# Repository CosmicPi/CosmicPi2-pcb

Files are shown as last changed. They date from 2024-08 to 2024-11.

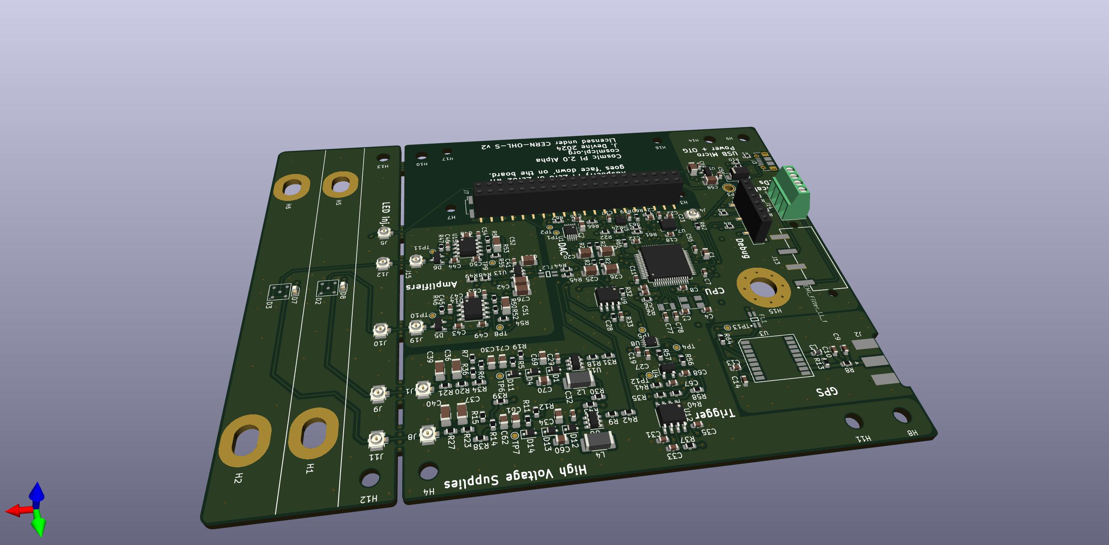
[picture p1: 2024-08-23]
3drenderthird.jpg

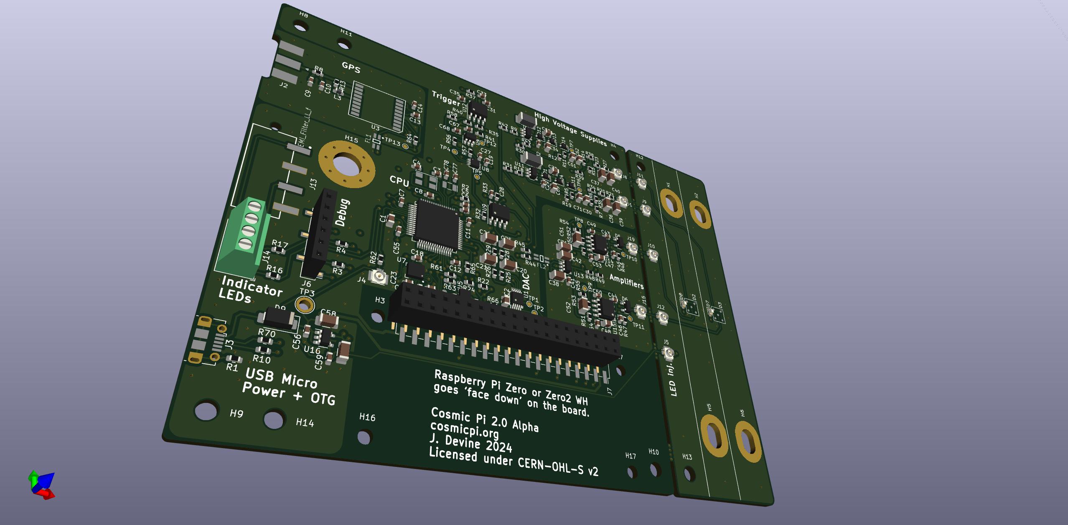
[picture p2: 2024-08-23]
3drendersecond.jpg

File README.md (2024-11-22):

# CosmicPiV2.0b
Version 2, beta production of the Cosmic Pi, learning the lessons from V2.0alpha and adding back the UART connection between GPS and STM32. All the components are now on a single PCB with a snap-off for the SiPM elements. SiPMs are now from Broadcom, as they purchased Ketek's SiPM production unit.

The design uses scintillators from Amcrys http://www.amcrys.com/ which are not yet available via a retail outlet, however any BC-408 equivalent scintillator that has diamond polished finish surfaces and dimensions of 200x100x10mm can be mated to the SiPMs with suitable mounting holes.

# What do the signals do?
To be added

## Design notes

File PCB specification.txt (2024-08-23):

Cosmic Pi PCB specification
Base material: FR-4
Number of layers: 4
PCB dimensions: 130mmx185mm
PCB thickness: 1.6mm
PCB colour: Green
Surface finish: HASL lead free
Minimum Solder Mask Dam: 0.4mm
Copper weight: 1 oz
Minimum Drill Hole Size: 0.3mm
Trace width/spaceing: 6/6 mil
Plated half holes/castellated holes: No
Impedance control: No

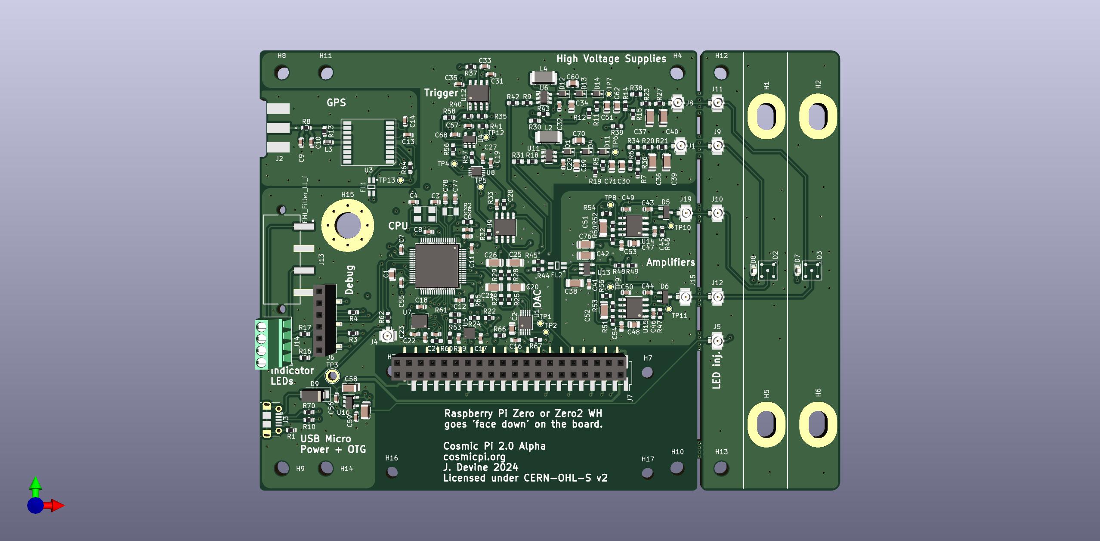
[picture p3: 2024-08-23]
3drenderfirst.jpg

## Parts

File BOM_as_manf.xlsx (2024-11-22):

Item # | *Designator | *Qty | Manufacturer | *Mfg Part # | Description / Value | *Package/Footprint | Category | Your Instructions / Notes
1 | J7 | 1 | Harwin | M20-7872042 | 40 pin socket (2x20) for Raspberry Pi Zero | PinSocket_2x20_P2.54mm_Vertical_SMD | SMD
2 | R1,R16,R4,R3,R17,R70,R10 | 7 | Yageo | RC0603FR-0720RL | 20 Ohm resistor, 1%, 0.1W | R_0603_1608Metric | SMD
3 | C71,C34,C69,C61 | 4 | Murata | GCJ21BR72A104KA01K | 1u, 100V DC, 10% | C_0805_2012Metric | SMD
4 | R62 | 1 | Yageo | RC0603JR-07300RL | 300 Ohm resistor, 1% | R_0603_1608Metric | SMD
5 | C40,C75,C25,C37,C26,C21,C20,C36,C42,C58,C38,C39 | 12 | KYOCERA AVX | 12061C105KAZ2A | 1u, 100V DC, 10% | C_1206_3216Metric | SMD
6 | C62,C30 | 2 | Kemet | C0805C473K1RACTU | 47n, 100V, 10% | C_0805_2012Metric | SMD
7 | D5,D6 | 2 | Vishay | BAS70-04-G3-08 |  | SOT-23 | SMD
8 | U14,U15 | 2 | Analog Devices | AD8538ARZ | AD8039 | SOIC-8_3.9x4.9mm_P1.27mm | SMD
9 | C23,C55,C35,C5,C14,C43,C15,C6,C18,C7,C27,C11,C67,C49,C53,C50,C44,C54,C12,C8,C17, C16 | 22 | Kemet | C0603C104K4RACTU | 100n, 16V, 10% | C_0603_1608Metric | SMD
10 | R22,R25,R28,R24,R26,R49,R35,R7,R29,R15 | 10 | ROHM | MCR03EZPFX2202 | 10k, 1% | R_0603_1608Metric | DNS | CRG0603F10K
11 | FL1,FL2 | 2 | Wurth | 744232090 | Wire wound EMI filter | IND_744232090 | SMD | DLW31SN900SQ2L
12 | C70,C60 | 2 | Samsung | CL21B104KBCNNNC | 0.1u, 50V, 10% | C_0805_2012Metric | SMD
13 | U5 | 1 | Bosch | BME280 | Bosch humidity sensor BME280 | Bosch_LGA-8_2.5x2.5mm_P0.65mm_ClockwisePinNumbering | SMD
14 | U6,U11 | 2 | Analog Devices | MAX5026EUT-T | MAX5026EUT_ | SOT-23-6 | SMD | MAX5026EUT+T
15 | R63,R34,R64,R36,R39,R31,R59,R66,R57,R44,R38,R42,R61,R45,R60,R67,R30,R56,R58,R43,R8,R68,R69 | 21 | Yageo | RC0603JR-070RL | 0 ohm jumper, 5%, 0.1W | R_0603_1608Metric_Pad0.98x0.95mm_HandSolder | SMD
16 | R46,R47 | 2 | Yageo | RC0603FR-075K1L | 5.1k Ohm resistor, 1%, 0.1W | R_0603_1608Metric | SMD
17 | U16,U13 | 2 | Texas Instruments | LP2985-33DBVR | LP2985-3.3 | SOT-23-5 | SMD
18 | J13 | 1 | Wurth | 691709710304 | 691709710304 wurth 4 pin screw terminal. | 691709710304 | TH
19 | C59,C31,C41,C22 | 4 | Samsung | CL10B103KB8NNNC | 10n, 10%, 50V | C_0603_1608Metric | SMD
20 | U12 | 1 | onsemi | LM555CM | LM555 timer IC | SOIC-8_3.9x4.9mm_P1.27mm | SMD | TLC555ID
21 | L4,L2 | 2 | Murata | #A915BY-470M=P3 | 47u, 750mA | D53LC, 2020 | SMD | A915BY-470M=P3
22 | C32,C29,C19,C28,C68 | 5 | Murata | GCM188R71E105KA64D | 1u, 10%, 25V | C_0603_1608Metric | SMD
23 | J5,J9,J1,J4,J11,J10,J15,J12,J19,J8 | 10 | Hirose | U.FL-R-SMT(01) | u.FL socket | U.FL_Hirose_U.FL-R-SMT-1_Vertical | SMD
24 | C46,C45 | 2 | Kemet | C0603C300J5GACTU | 30p, 5%, 50V | C_0603_1608Metric | SMD
25 | D11,D12,D1,D4,D14,D13 | 6 | onsemi | 1N4148WS | 1N4148 | D_SOD-323F | SMD
26 | Y2 | 1 | Euroquartz | EQ161-32.768-9 | 32.768KHz | Crystal_SMD_EuroQuartz_EQ161-2Pin_3.2x1.5mm | SMD | ABS07-32.768KHZ-9-T
27 | R50,R21,R27,R20,R51,R23 | 6 | TE conectivity | CRG0603F1K0 | 1k, 1% 0.1W | R_0603_1608Metric | SMD
28 | R48 | 1 | Panasonic | ERA3AEB203V | 20k, 0.1%, 0.1W | R_0603_1608Metric | SMD
29 | C13,C24, C2 | 3 | Murata | GRM188R61A106ME69D | 10u, 10%, 10V | C_0603_1608Metric | SMD
30 | C77,C78 | 2 | TDK | CGA3E2C0G2A040C080AA | 4.3p, 100V | C_0603_1608Metric | SMD
31 | L3 | 1 | EPCOS | B82496C3470J000 | 47nH | L_0603_1608Metric | SMD
32 | C4,C3 | 2 | Syfer | 0603Y1000220JCT | 22p, 5%, 100V | C_0603_1608Metric | SMD
33 | C1 | 1 | Samsung | CL21B475KOFNNNG | 4.7u, 10%, 16V | C_0805_2012Metric | SMD
34 | R32,R33 | 2 | TE conectivity | CRG0603F330R | 330R, 1% 0.1W | R_0603_1608Metric | SMD | RC0603JR-07300RL
35 | R52,R53 | 2 | Panasonic | ERA3AEB303V | 30k, 0.1%, 0.1W | R_0603_1608Metric | SMD
36 | C47,C48 | 2 | Yageo | CC0603KRX7R9BB104 | 100n, 50V, 10% | C_0805_2012Metric | SMD | C0805C104K5RACTU
37 | Y1 | 1 | RALTRON | QC5CA8.00000F12B23R | 8 MHz | Crystal_SMD_5032-4Pin_5.0x3.2mm | SMD | LFXTAL061627
38 | D9 | 1 | Vishay | B140-E3/61T | B140-E3 | D_SMA | SMD
39 | R41,R37,R40,R2 | 4 | Vishay | CRCW0603100KFKEA | 100k, 1%, 0.1W | R_0603_1608Metric | SMD
40 | J3 | 1 | Molex | 105017-0001 | USB_B_Micro | USB_Micro-B_Molex-105017-0001 | SMD | 1050170001
41 | U9 | 1 | Maxim | MAX991ESA+ | MAX991 | SOIC-8_3.9x4.9mm_P1.27mm | SMD
42 | U7 | 1 | ST | LSM9DS1TR | LSM9DS1 | LGA-24L_3x3.5mm_P0.43mm | SMD
43 | R6,R14 | 2 | Vishay | CRCW0603200KFKEA | 200k, 1%, 0.1W | R_0603_1608Metric | SMD
44 | D8,D7 | 2 | Kingbright | KPH-1608QBC-D | LED | LED_0603_1608Metric | SMD | 150060BS84000
45 | R54,R55 | 2 | Panasonic | ERJ3EKF1000V | 100, 1%, 0.1W | R_0603_1608Metric | SMD
46 | J6 | 1 | Multicomp | 2211SM-06G-B1-TB | Programming header | PinSocket_1x06_P2.54mm_Vertical_SMD_Pin1Left | SMD
47 | C56 | 1 | TDK | C1608X5R1A226M080AC | 22u, 10V, 20% | C_0603_1608Metric | SMD
48 | J2 | 1 | Molex | 73251-1150 | SMA | SMA_Molex_73251-1153_EdgeMount_Horizontal | Edge
49 | U3 | 1 | Quectel | L76-M33 | L76-M33 | LM76-M33 | SMD
50 | U8 | 1 | Texas Instruments | SN74AUC2G32DCUR | 74AUC2G32 | VSSOP-8_2.4x2.1mm_P0.5mm | SMD
51 | R12,R19 | 2 | Vishay | CRCW06036K81FKEA | 6.81k, 1% 0.1W | R_0603_1608Metric | SMD
52 | U1 | 1 | Microchip | MCP4728-E/UN | MCP4728 | MSOP-10_3x3mm_P0.5mm | SMD
53 | R5,R11 | 2 | TE conectivity | CPF0603B255KE1 | 255k, 1%, 0.063W | R_0603_1608Metric | SMD
54 | U4 | 1 | Diodes incorporated | 74AHC1G00W5-7 | 74AHC1G00 | SOT-23-5 | SMD
55 | C76 | 1 | Taiyo Yuden | JMK316BBJ107MLHT | 100u, 20%, 6.3V | C_1206_3216Metric | SMD
56 | R13 | 1 | Vishay | CRCW060310R0FKEA | 10, 1%, 0.1W | R_0603_1608Metric | SMD
57 | U2 | 1 | ST | STM32F401RET6 | STM32F401RETx | LQFP-64_10x10mm_P0.5mm | SMD
58 | R9,R18 | 2 | Panasonic | ERA3AEB1372V | 13.7k, 0.1%, 0.1W | R_0603_1608Metric | SMD | ERA-3AEB1372V
59 | D2,D3 | 2 | Broadcom | AFBR-S4N44P014M | SiPM diode for single photon detection | AFBR-S4N44P014M | SMD
60 | C33 | 1 | Yageo | CC0603KRX7R8BB224 | 220n, 25V 10% | C_0603_1608Metric | SMD

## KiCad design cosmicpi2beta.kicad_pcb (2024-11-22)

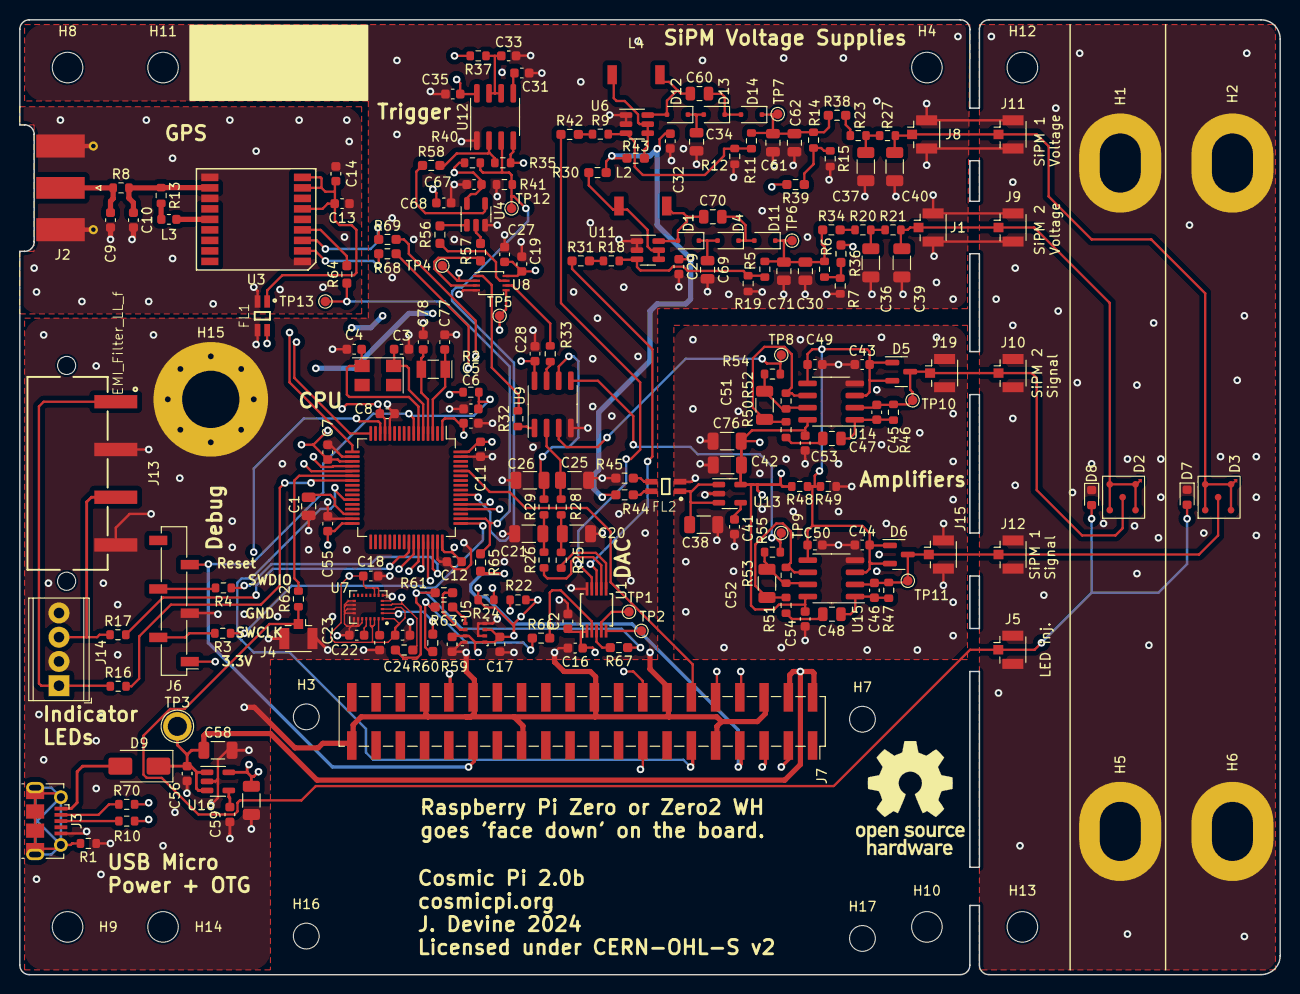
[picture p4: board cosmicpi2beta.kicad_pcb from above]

Board: 4 copper layers, 132.0 x 100.0 mm, 221 parts (0 on the bottom side), 122 nets.

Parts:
C1: 4.7u; C_0805_2012Metric
C2, C13, C24: 10u; C_0603_1608Metric
C3, C4: 22p; C_0603_1608Metric
C5, C6, C7, C8, C11, C12, C14, C15, C16, C17, C18, C23, C27, C35, C43, C44, C49, C50, C53, C54, C55, C67: 100n; C_0603_1608Metric
C9, C10: n.a.; C_0603_1608Metric
C19, C28, C29, C32, C68: 1u; C_0603_1608Metric
C20, C21, C25, C26, C36, C37, C38, C39, C40, C42, C58, C75: 1u; C_1206_3216Metric
C22, C31, C41, C59: 10n; C_0603_1608Metric
C30, C62: 47n, 100V; C_0805_2012Metric
C33: 220n; C_0603_1608Metric
C34, C61, C69, C71: 1u, 100V; C_0805_2012Metric
C45, C46: 30p; C_0603_1608Metric
C47, C48: 100n; C_0805_2012Metric
C51, C52: n.a.; C_1206_3216Metric
C56: 22u; C_0603_1608Metric
C60, C70: 0.1u, 50V; C_0805_2012Metric
C76: 100u; C_1206_3216Metric
C77, C78: 4.3p; C_0603_1608Metric
D1, D4, D11, D12, D13, D14: 1N4148; D_SOD-323F
D2, D3: D; AFBR-S4N44P014M
D5, D6: BAS70-04; SOT-23
D7, D8: LED; LED_0603_1608Metric
D9: B140-E3; D_SMA
FL1, FL2: EMI_Filter_LL_f; IND_744232090
H1, H2, H5, H6: SiPM_Bracket; MountingHole_4.3x6.2mm_M4_Pad
H3, H7, H16, H17: RPi; MountingHole_2.7mm_M2.5_DIN965
H4, H8, H9, H10, H11, H12, H13, H14: MountingHole; MountingHole_3.2mm_M3_DIN965
H15: Cable_pass; MountingHole_6mm_Pad_Via
J1, J4, J5, J8, J9, J10, J11, J12, J15, J19: u.FL; U.FL_Hirose_U.FL-R-SMT-1_Vertical
J2: SMA; SMA_Molex_73251-1153_EdgeMount_Horizontal
J3: USB_B_Micro; USB_Micro-B_Molex-105017-0001
J6: SWD; PinSocket_1x06_P2.54mm_Vertical_SMD_Pin1Left
J7: Raspberry_Pi_2_3_Zero; PinSocket_2x20_P2.54mm_Vertical_SMD
J13: 691709710304
J14: Screw_Terminal_01x04; TerminalBlock_Phoenix_MPT-0,5-4-2.54_1x04_P2.54mm_Horizontal
L2, L4: 47u; Inductor_#A915BY-470M=P3
L3: 47nH; L_0603_1608Metric
R1, R3, R4, R10, R16, R17, R70: 20; R_0603_1608Metric
R2, R37, R40, R41: 100k; R_0603_1608Metric
R5, R11: 255k; R_0603_1608Metric
R6, R14: 200k; R_0603_1608Metric
R7, R15, R22, R24, R25, R26, R28, R29, R35, R49: 10k; R_0603_1608Metric
R8: 0; R_0603_1608Metric
R9, R18: 13.7k; R_0603_1608Metric
R12, R19: 6.81k; R_0603_1608Metric
R13: 10; R_0603_1608Metric
R20, R21, R23, R27, R50, R51: 1k; R_0603_1608Metric
R30, R31, R34, R36, R38, R39, R42, R43, R44, R45, R56, R57, R58, R59, R60, R61, R63, R64, R66, R67, R68, R69: 0; R_0603_1608Metric_Pad0.98x0.95mm_HandSolder
R32, R33: 330R; R_0603_1608Metric
R46, R47: 5100; R_0603_1608Metric
R48: 20k; R_0603_1608Metric
R52, R53: 30k; R_0603_1608Metric
R54, R55: 100; R_0603_1608Metric
R62: 300; R_0603_1608Metric
R65: DNP; R_0603_1608Metric_Pad0.98x0.95mm_HandSolder
TP1, TP2, TP4, TP5, TP6, TP7, TP8, TP9, TP10, TP11, TP12, TP13: TestPoint; TestPoint_Pad_D1.0mm
TP3: TestPoint; TestPoint_Plated_Hole_D2.0mm
U1: MCP4728; MSOP-10_3x3mm_P0.5mm
U2: STM32F401RETx; LQFP-64_10x10mm_P0.5mm
U3: L76-M33; LM76-M33
U4: 74AHC1G00; SOT-23-5
U5: BME280; Bosch_LGA-8_2.5x2.5mm_P0.65mm_ClockwisePinNumbering
U6, U11: MAX5026EUT_; SOT-23-6
U7: LSM9DS1; LGA-24L_3x3.5mm_P0.43mm
U8: 74AUC2G32; VSSOP-8_2.4x2.1mm_P0.5mm
U9: MAX991; SOIC-8_3.9x4.9mm_P1.27mm
U12: LM555; SOIC-8_3.9x4.9mm_P1.27mm
U13, U16: LP2985-3.3; SOT-23-5
U14, U15: AD8039; SOIC-8_3.9x4.9mm_P1.27mm
Y1: 8 MHz; Crystal_SMD_5032-4Pin_5.0x3.2mm
Y2: 32.768KHz; Crystal_SMD_EuroQuartz_EQ161-2Pin_3.2x1.5mm

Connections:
+3.3VA: C42.1, C53.1, C54.1, C76.1, R48.1, U13.5 (VOUT), U14.8 (V+), U15.8 (V+)
+3V3: C2.1, C6.1, C7.1, C8.1, C11.1, C12.1, C15.2, C16.1, C17.2, C18.2, C19.1, C24.2, C27.1, C28.2, C35.1, C55.1, C67.1, C68.1, C75.1, FL1.2, J6.1, R2.1, R22.2, R24.2, R35.2, R37.2, R40.2, U1.1 (VDD), U2.1 (VBAT), U2.13 (VREF+), U2.19 (VDD), U2.32 (VDD), U2.48 (VDD), U2.64 (VDD), U4.5 (VCC), U5.2 (CSB), U5.6 (VDDIO), U5.8 (VDD), U7.1 (VDDIO), U7.3 (VDDIO), U7.7 (CS_A/G), U7.8 (CS_M), U7.22 (VDD), U7.23 (VDD), U8.8 (VCC), U9.8 (V+), U12.4 (R), U12.8 (VCC), U16.5 (VOUT)
+5V: C29.1, C32.1, C56.2, C58.1, D9.1 (K), J7.2 (5V), J7.4 (5V), R30.1, R43.1, R44.1, TP3.1, U16.1 (VIN), U16.3 (ON/~OFF)
/analog/SIGNAL_OUT_1: R54.2, TP8.1, U9.3 (+)
/analog/SIGNAL_OUT_2: R55.2, TP9.1, U9.5 (+)
BIASFB0: R36.2, U2.20 (PA4)
BIASFB1: R39.2, U2.21 (PA5)
BOOT0: J7.12 (GPIO18/PWM0), U2.60 (BOOT0)
CH_A_OR: TP4.1, U2.52 (PC11), U8.2
CH_B_OR: TP5.1, U2.53 (PC12), U8.5
DAC0: R25.1, U1.6 (VOUTA)
DAC1: R26.1, U1.7 (VOUTB)
FLAG: J7.11 (GPIO17), U2.27 (PB1)
GND: C1.2, C2.2, C3.2, C4.2, C5.2, C6.2, C7.2, C8.2, C11.2, C12.2, C15.1, C16.2, C17.1, C18.1, C19.2, C20.2, C21.2, C22.1, C23.1, C24.1, C25.2, C26.2, C27.2, C28.1, C29.2, C30.1, C31.2, C32.2, C33.2, C34.2, C35.2, C36.2, C37.2, C39.2, C40.2, C55.2, C56.1, C58.2, C59.2, C61.1, C62.1, C67.2, C68.2, C69.2, C71.1, C75.2, C77.2, C78.2, D7.1 (K), D8.1 (K), FL1.3, H1.1, H2.1, H5.1, H6.1, H15.1, J1.2 (Ext), J3.5 (GND), J4.2 (Ext), J5.2 (Ext), J6.3, J7.6 (GND), J7.9 (GND), J7.14 (GND), J7.20 (GND), J7.25 (GND), J7.30 (GND), J7.34 (GND), J7.39 (GND), J8.2 (Ext), J9.2 (Ext), J10.2 (Ext), J11.2 (Ext), J12.2 (Ext), J13.2, J13.4, J14.2, J14.4, R1.1, R7.2, R12.2, R15.2, R19.2, R41.1, R45.1, U1.10 (VSS), U2.12 (VSSA), U2.18 (VSS), U2.31 (VSS), U2.47 (VSS), U2.63 (VSS), U4.3 (GND), U5.1 (GND), U5.5 (SDO), U5.7 (GND), U6.1 (PGND), U6.2 (GND), U7.5 (SDO_A/G), U7.6 (SDO_M), U7.14 (RES), U7.15 (RES), U7.16 (RES), U7.17 (RES), U7.18 (RES), U7.19 (GND), U7.20 (GND), U8.4 (GND), U9.4 (V-), U11.1 (PGND), U11.2 (GND), U12.1 (GND), U16.2 (GND)
GNDD: C9.2, C10.2, C13.2, C14.2, FL1.4, J2.2 (Ext), U3.1 (GND), U3.10 (GND), U3.12 (GND)
GNDREF: C38.2, C41.2, C42.2, C43.1, C44.1, C49.1, C50.1, C53.2, C54.2, C76.2, FL2.4, J15.2 (Ext), J19.2 (Ext), R49.2, U13.2 (GND), U14.4 (V-), U15.4 (V-)
GPSPPS: R64.2, U3.4 (1PPS)
GPSRX: R69.1, U2.16 (PA2), U3.3 (RXD1)
GPSTX: R68.1, U2.17 (PA3), U3.2 (TDX1)
HV_DAC0: R31.1, U1.8 (VOUTC)
HV_DAC1: R42.1, U1.9 (VOUTD)
INJ_LED: R62.2, U2.22 (PA6)
LED_Test_A: D7.2 (A), D8.2 (A), J4.1 (In), J5.1 (In), R62.1
unnamed: C20.1, R25.2, R28.1
unnamed: C21.1, R26.2, R29.1
unnamed: C36.1, R20.2, R21.1
unnamed: C37.1, R23.2, R27.1
unnamed: C45.1, C47.2, R46.2, U14.1
unnamed: C46.1, C48.2, R47.2, U15.1
unnamed: C47.1, R50.1
unnamed: C48.1, R51.1
unnamed: C51.1, R52.2, R54.1, U14.7
unnamed: C52.1, R53.2, R55.1, U15.7
unnamed: C70.1, D1.2 (A), L2.2, U11.6 (LX)
unnamed: C69.1, D1.1 (K), D4.2 (A)
unnamed: D9.2 (A), J3.1 (VBUS)
unnamed: C70.2, D4.1 (K), D11.2 (A)
unnamed: C30.2, C71.2, D11.1 (K), R5.1, R6.1, R34.1, TP6.1
unnamed: C60.1, D12.2 (A), L4.2, U6.6 (LX)
unnamed: C34.1, D12.1 (K), D13.2 (A)
unnamed: C60.2, D13.1 (K), D14.2 (A)
unnamed: C61.2, C62.2, D14.1 (K), R11.1, R14.1, R38.1, TP7.1
unnamed: FL2.2, R44.2
unnamed: FL2.3, R45.2
unnamed: C9.1, J2.1 (In), R8.1
unnamed: J3.3 (D+), R10.1
unnamed: J3.2 (D-), R70.1
unnamed: J3.6 (Shield), R1.2
unnamed: J6.2, R3.2
unnamed: J6.4, R4.2
unnamed: J7.15 (GPIO22), R68.2
unnamed: J7.16 (GPIO23), R69.2
unnamed: J13.1, J14.1, R16.1
unnamed: J13.3, J14.3, R17.1
unnamed: L3.1, R13.2
unnamed: R14.2, R15.1, R39.1
unnamed: R18.1, R31.2
unnamed: R32.1, U9.1
unnamed: R32.2, U8.1
unnamed: R33.1, U9.7
unnamed: R33.2, U8.6
unnamed: R6.2, R7.1, R36.1
unnamed: R9.1, R42.2
unnamed: R56.1, U4.1
unnamed: R56.2, U8.7
unnamed: R57.1, U4.2
unnamed: R57.2, U8.3
unnamed: R58.1, U4.4
unnamed: TP2.1, U1.5 (RDY/~BSY)
unnamed: R66.2, U1.2 (SCL)
unnamed: R67.2, U1.3 (SDA)
unnamed: TP1.1, U1.4 (~LDAC)
unnamed: R64.1, R65.1, TP13.1, U2.50 (PA15)
unnamed: C77.1, U2.3 (PC14), Y2.1
unnamed: C78.1, U2.4 (PC15), Y2.2
unnamed: C3.1, U2.5 (PH0), Y1.1
unnamed: C4.1, U2.6 (PH1), Y1.2
unnamed: C1.1, U2.30 (VCAP1)
unnamed: C13.1, C14.1, FL1.1, U3.6 (V_BCKP), U3.8 (VCC), U3.9 (RESET)
unnamed: C10.1, R8.2, R13.1, U3.11 (RF_IN)
unnamed: L3.2, U3.14 (VCC_RF)
unnamed: R63.1, U5.4 (SCK)
unnamed: R61.1, U5.3 (SDI)
unnamed: R9.2, R11.2, R12.1, U6.3 (FB)
unnamed: L4.1, R43.2, U6.4 (~SHDN), U6.5 (VCC)
unnamed: C23.2, U7.24 (C1)
unnamed: C22.2, U7.21 (CAP)
unnamed: R22.1, R59.2, U7.2 (SCL/SPC)
unnamed: R24.1, R60.2, U7.4 (SDA/SDI/SDO)
unnamed: C25.1, R28.2, U9.2 (-)
unnamed: C26.1, R29.2, U9.6 (-)
unnamed: R5.2, R18.2, R19.1, U11.3 (FB)
unnamed: L2.1, R30.2, U11.4 (~SHDN), U11.5 (VCC)
unnamed: C31.1, U12.5 (CV)
unnamed: C33.1, R37.1, U12.6 (THR), U12.7 (DIS)
unnamed: R35.1, R58.2, U12.2 (TR)
unnamed: C41.1, U13.4 (BP)
unnamed: C38.1, FL2.1, U13.1 (VIN), U13.3 (ON/~OFF)
unnamed: C51.2, R50.2, R52.1, U14.6 (-)
unnamed: C52.2, R51.2, R53.1, U15.6 (-)
unnamed: C59.1, U16.4 (BP)
RPI_Time: J7.7 (GCLK0/GPIO4), R65.2
RPI_extra: J7.32 (PWM0/GPIO12), U2.14 (PA0)
RX0: J7.8 (GPIO14/TXD), U2.43 (PA10)
SCL0: J7.5 (SCL/GPIO3), R59.1, R63.2, R66.1
SDA0: J7.3 (SDA/GPIO2), R60.1, R61.2, R67.1
SWCLK: R3.1, U2.49 (PA14)
SWDIO: R4.1, U2.46 (PA13)
SiPM1_test_A: C45.2, D2.2 (A), D5.3, J10.1 (In), J19.1 (In), R46.1, TP10.1, U14.2 (-)
SiPM1_test_K: C39.1, D2.1 (K), J1.1 (In), J9.1 (In), R21.2
SiPM2_test_A: C46.2, D3.2 (A), D6.3, J12.1 (In), J15.1 (In), R47.1, TP11.1, U15.2 (-)
SiPM2_test_K: C40.1, D3.1 (K), J8.1 (In), J11.1 (In), R27.2
TRIG_OUT: R40.1, R41.2, TP12.1, U2.55 (PB3), U12.3 (Q)
TX0: J7.10 (GPIO15/RXD), U2.42 (PA9)
USB_OTG_DM: R70.2, U2.44 (PA11)
USB_OTG_DP: R10.2, U2.45 (PA12)
VBIAS1: R20.1, R34.2
VBIAS2: R23.1, R38.2
V_OFFSET: C43.2, C44.2, C49.2, C50.2, D5.1, D5.2, D6.1, D6.2, R48.2, R49.1, U14.3 (+), U14.5 (+), U15.3 (+), U15.5 (+)
_RESET: C5.1, J6.5, J7.29 (GCLK1/GPIO5), R2.2, U2.7 (NRST)
evt_led: R17.2, U2.41 (PA8)
pwr_led: R16.2, U2.23 (PA7)

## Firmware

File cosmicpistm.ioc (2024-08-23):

#MicroXplorer Configuration settings - do not modify
ADC1.Channel-0\#ChannelRegularConversion=ADC_CHANNEL_0
ADC1.IPParameters=Rank-0\#ChannelRegularConversion,master,Channel-0\#ChannelRegularConversion,SamplingTime-0\#ChannelRegularConversion,NbrOfConversionFlag
ADC1.NbrOfConversionFlag=1
ADC1.Rank-0\#ChannelRegularConversion=1
ADC1.SamplingTime-0\#ChannelRegularConversion=ADC_SAMPLETIME_3CYCLES
ADC1.master=1
File.Version=6
KeepUserPlacement=false
Mcu.Family=STM32F4
Mcu.IP0=ADC1
Mcu.IP1=I2C1
Mcu.IP2=NVIC
Mcu.IP3=RCC
Mcu.IP4=SYS
Mcu.IP5=TIM2
Mcu.IP6=TIM3
Mcu.IP7=USART1
Mcu.IP8=USART2
Mcu.IP9=USB_OTG_FS
Mcu.IPNb=10
Mcu.Name=STM32F401R(D-E)Tx
Mcu.Package=LQFP64
Mcu.Pin0=PC14-OSC32_IN
Mcu.Pin1=PC15-OSC32_OUT
Mcu.Pin10=PA3
Mcu.Pin11=PA4
Mcu.Pin12=PA5
Mcu.Pin13=PA6
Mcu.Pin14=PA7
Mcu.Pin15=PB1
Mcu.Pin16=PB13
Mcu.Pin17=PC7
Mcu.Pin18=PC8
Mcu.Pin19=PA8
Mcu.Pin2=PH0 - OSC_IN
Mcu.Pin20=PA9
Mcu.Pin21=PA10
Mcu.Pin22=PA11
Mcu.Pin23=PA12
Mcu.Pin24=PA13
Mcu.Pin25=PA14
Mcu.Pin26=PA15
Mcu.Pin27=PC11
Mcu.Pin28=PC12
Mcu.Pin29=PB3
Mcu.Pin3=PH1 - OSC_OUT
Mcu.Pin30=PB7
Mcu.Pin31=PB8
Mcu.Pin32=VP_ADC1_TempSens_Input
Mcu.Pin33=VP_SYS_VS_Systick
Mcu.Pin34=VP_TIM2_VS_ClockSourceINT
Mcu.Pin35=VP_TIM3_VS_ClockSourceINT
Mcu.Pin4=PC1
Mcu.Pin5=PC2
Mcu.Pin6=PC3
Mcu.Pin7=PA0-WKUP
Mcu.Pin8=PA1
Mcu.Pin9=PA2
Mcu.PinsNb=36
Mcu.ThirdPartyNb=0
Mcu.UserConstants=
Mcu.UserName=STM32F401RETx
MxCube.Version=5.2.1
MxDb.Version=DB.5.0.21
NVIC.BusFault_IRQn=true\:0\:0\:false\:false\:true\:false\:false
NVIC.DebugMonitor_IRQn=true\:0\:0\:false\:false\:true\:false\:false
NVIC.HardFault_IRQn=true\:0\:0\:false\:false\:true\:false\:false
NVIC.MemoryManagement_IRQn=true\:0\:0\:false\:false\:true\:false\:false
NVIC.NonMaskableInt_IRQn=true\:0\:0\:false\:false\:true\:false\:false
NVIC.PendSV_IRQn=true\:0\:0\:false\:false\:true\:false\:false
NVIC.PriorityGroup=NVIC_PRIORITYGROUP_4
NVIC.SVCall_IRQn=true\:0\:0\:false\:false\:true\:false\:false
NVIC.SysTick_IRQn=true\:0\:0\:false\:false\:true\:false\:true
NVIC.UsageFault_IRQn=true\:0\:0\:false\:false\:true\:false\:false
PA0-WKUP.GPIOParameters=GPIO_Label
PA0-WKUP.GPIO_Label=shaped_out_1
PA0-WKUP.Locked=true
PA0-WKUP.Signal=ADCx_IN0
PA1.GPIOParameters=GPIO_Label
PA1.GPIO_Label=shaped_out_2
PA1.Locked=true
PA1.Signal=ADCx_IN1
PA10.Locked=true
PA10.Mode=Asynchronous
PA10.Signal=USART1_RX
PA11.Locked=true
PA11.Mode=Device_Only
PA11.Signal=USB_OTG_FS_DM
PA12.Locked=true
PA12.Mode=Device_Only
PA12.Signal=USB_OTG_FS_DP
PA13.Locked=true
PA13.Mode=Serial_Wire
PA13.Signal=SYS_JTMS-SWDIO
PA14.Locked=true
PA14.Mode=Serial_Wire
PA14.Signal=SYS_JTCK-SWCLK
PA15.GPIOParameters=GPIO_Label
PA15.GPIO_Label=GPSPPS
PA15.Locked=true
PA15.Signal=S_TIM2_CH1_ETR
PA2.GPIOParameters=GPIO_Label
PA2.GPIO_Label=gpsrx
PA2.Locked=true
PA2.Mode=Asynchronous
PA2.Signal=USART2_TX
PA3.GPIOParameters=GPIO_Label
PA3.GPIO_Label=gpstx
PA3.Locked=true
PA3.Mode=Asynchronous
PA3.Signal=USART2_RX
PA4.GPIOParameters=GPIO_Label
PA4.GPIO_Label=biasfb1
PA4.Locked=true
PA4.Signal=ADCx_IN4
PA5.GPIOParameters=GPIO_Label
PA5.GPIO_Label=biasfb2
PA5.Locked=true
PA5.Signal=ADCx_IN5
PA6.GPIOParameters=GPIO_Label
PA6.GPIO_Label=inj_led
PA6.Locked=true
PA6.Signal=S_TIM3_CH1
PA7.GPIOParameters=GPIO_Label
PA7.GPIO_Label=pwr_led
PA7.Locked=true
PA7.Signal=GPIO_Output
PA8.GPIOParameters=GPIO_Label
PA8.GPIO_Label=evt_led
PA8.Locked=true
PA8.Signal=GPIO_Output
PA9.Locked=true
PA9.Mode=Asynchronous
PA9.Signal=USART1_TX
PB1.GPIOParameters=GPIO_Label
PB1.GPIO_Label=flag
PB1.Locked=true
PB1.Signal=GPIO_Output
PB13.GPIOParameters=GPIO_Label
PB13.GPIO_Label=hvpsu_sclk
PB13.Locked=true
PB13.Signal=GPIO_Output
PB3.GPIOParameters=GPIO_Label
PB3.GPIO_Label=trig_out
PB3.Locked=true
PB3.Signal=S_TIM2_CH2
PB7.Locked=true
PB7.Mode=I2C
PB7.Signal=I2C1_SDA
PB8.Locked=true
PB8.Mode=I2C
PB8.Signal=I2C1_SCL
PC1.GPIOParameters=GPIO_Label
PC1.GPIO_Label=hvpsu_cl1
PC1.Locked=true
PC1.Signal=GPIO_Input
PC11.GPIOParameters=GPIO_Label
PC11.GPIO_Label=strigout_b
PC11.Locked=true
PC11.Signal=GPIO_Input
PC12.GPIOParameters=GPIO_Label
PC12.GPIO_Label=strigout_a
PC12.Locked=true
PC12.Signal=GPIO_Input
PC14-OSC32_IN.Locked=true
PC14-OSC32_IN.Mode=LSE-External-Oscillator
PC14-OSC32_IN.Signal=RCC_OSC32_IN
PC15-OSC32_OUT.Locked=true
PC15-OSC32_OUT.Mode=LSE-External-Oscillator
PC15-OSC32_OUT.Signal=RCC_OSC32_OUT
PC2.GPIOParameters=GPIO_Label
PC2.GPIO_Label=hvpsu_cl2
PC2.Locked=true
PC2.Signal=GPIO_Input
PC3.GPIOParameters=GPIO_Label
PC3.GPIO_Label=hvpsu_din
PC3.Locked=true
PC3.Signal=GPIO_Output
PC7.GPIOParameters=GPIO_Label
PC7.GPIO_Label=hvpsu_cs2
PC7.Locked=true
PC7.Signal=GPIO_Output
PC8.GPIOParameters=GPIO_Label
PC8.GPIO_Label=hvpsu_cs1
PC8.Locked=true
PC8.Signal=GPIO_Output
PCC.Checker=false
PCC.Line=STM32F401
PCC.MCU=STM32F401R(D-E)Tx
PCC.PartNumber=STM32F401RETx
PCC.Seq0=0
PCC.Series=STM32F4
PCC.Temperature=25
PCC.Vdd=3.3
PH0\ -\ OSC_IN.Locked=true
PH0\ -\ OSC_IN.Mode=HSE-External-Oscillator
PH0\ -\ OSC_IN.Signal=RCC_OSC_IN
PH1\ -\ OSC_OUT.Locked=true
PH1\ -\ OSC_OUT.Mode=HSE-External-Oscillator
PH1\ -\ OSC_OUT.Signal=RCC_OSC_OUT
PinOutPanel.RotationAngle=0
ProjectManager.AskForMigrate=true
ProjectManager.BackupPrevious=false
ProjectManager.CompilerOptimize=6
ProjectManager.ComputerToolchain=false
ProjectManager.CoupleFile=false
ProjectManager.CustomerFirmwarePackage=
ProjectManager.DefaultFWLocation=true
ProjectManager.DeletePrevious=true
ProjectManager.DeviceId=STM32F401RETx
ProjectManager.FirmwarePackage=STM32Cube FW_F4 V1.24.1
ProjectManager.FreePins=false
ProjectManager.HalAssertFull=false
ProjectManager.HeapSize=0x200
ProjectManager.KeepUserCode=true
ProjectManager.LastFirmware=true
ProjectManager.LibraryCopy=0
ProjectManager.MainLocation=Src
ProjectManager.NoMain=false
ProjectManager.PreviousToolchain=
ProjectManager.ProjectBuild=false
ProjectManager.ProjectFileName=cosmicpiv1point7.ioc
ProjectManager.ProjectName=cosmicpiv1point7
ProjectManager.StackSize=0x400
ProjectManager.TargetToolchain=EWARM V8
ProjectManager.ToolChainLocation=
ProjectManager.UnderRoot=false
ProjectManager.functionlistsort=1-SystemClock_Config-RCC-false-HAL-false
RCC.48MHZClocksFreq_Value=48000000
RCC.AHBFreq_Value=84000000
RCC.APB1CLKDivider=RCC_HCLK_DIV2
RCC.APB1Freq_Value=42000000
RCC.APB1TimFreq_Value=84000000
RCC.APB2Freq_Value=84000000
RCC.APB2TimFreq_Value=84000000
RCC.CortexFreq_Value=84000000
RCC.FCLKCortexFreq_Value=84000000
RCC.HCLKFreq_Value=84000000
RCC.HSE_VALUE=20000000
RCC.HSI_VALUE=16000000
RCC.I2SClocksFreq_Value=192000000
RCC.IPParameters=48MHZClocksFreq_Value,AHBFreq_Value,APB1CLKDivider,APB1Freq_Value,APB1TimFreq_Value,APB2Freq_Value,APB2TimFreq_Value,CortexFreq_Value,FCLKCortexFreq_Value,HCLKFreq_Value,HSE_VALUE,HSI_VALUE,I2SClocksFreq_Value,LSI_VALUE,MCO2PinFreq_Value,PLLCLKFreq_Value,PLLM,PLLN,PLLP,PLLQ,PLLQCLKFreq_Value,RTCFreq_Value,RTCHSEDivFreq_Value,SYSCLKFreq_VALUE,SYSCLKSource,VCOI2SOutputFreq_Value,VCOInputFreq_Value,VCOOutputFreq_Value,VcooutputI2S
RCC.LSI_VALUE=32000
RCC.MCO2PinFreq_Value=84000000
RCC.PLLCLKFreq_Value=84000000
RCC.PLLM=10
RCC.PLLN=168
RCC.PLLP=RCC_PLLP_DIV4
RCC.PLLQ=7
RCC.PLLQCLKFreq_Value=48000000
RCC.RTCFreq_Value=32000
RCC.RTCHSEDivFreq_Value=10000000
RCC.SYSCLKFreq_VALUE=84000000
RCC.SYSCLKSource=RCC_SYSCLKSOURCE_PLLCLK
RCC.VCOI2SOutputFreq_Value=384000000
RCC.VCOInputFreq_Value=2000000
RCC.VCOOutputFreq_Value=336000000
RCC.VcooutputI2S=192000000
SH.ADCx_IN0.0=ADC1_IN0,IN0
SH.ADCx_IN0.ConfNb=1
SH.ADCx_IN1.0=ADC1_IN1,IN1
SH.ADCx_IN1.ConfNb=1
SH.ADCx_IN4.0=ADC1_IN4,IN4
SH.ADCx_IN4.ConfNb=1
SH.ADCx_IN5.0=ADC1_IN5,IN5
SH.ADCx_IN5.ConfNb=1
SH.S_TIM2_CH1_ETR.0=TIM2_CH1,Input_Capture1_from_TI1
SH.S_TIM2_CH1_ETR.ConfNb=1
SH.S_TIM2_CH2.0=TIM2_CH2,Input_Capture2_from_TI2
SH.S_TIM2_CH2.ConfNb=1
SH.S_TIM3_CH1.0=TIM3_CH1,PWM Generation1 CH1
SH.S_TIM3_CH1.ConfNb=1
TIM2.Channel-Input_Capture1_from_TI1=TIM_CHANNEL_1
TIM2.Channel-Input_Capture2_from_TI2=TIM_CHANNEL_2
TIM2.IPParameters=Channel-Input_Capture1_from_TI1,Channel-Input_Capture2_from_TI2
TIM3.Channel-PWM\ Generation1\ CH1=TIM_CHANNEL_1
TIM3.IPParameters=Channel-PWM Generation1 CH1
USART1.IPParameters=VirtualMode
USART1.VirtualMode=VM_ASYNC
USART2.IPParameters=VirtualMode
USART2.VirtualMode=VM_ASYNC
USB_OTG_FS.IPParameters=VirtualMode
USB_OTG_FS.VirtualMode=Device_Only
VP_ADC1_TempSens_Input.Mode=IN-TempSens
VP_ADC1_TempSens_Input.Signal=ADC1_TempSens_Input
VP_SYS_VS_Systick.Mode=SysTick
VP_SYS_VS_Systick.Signal=SYS_VS_Systick
VP_TIM2_VS_ClockSourceINT.Mode=Internal
VP_TIM2_VS_ClockSourceINT.Signal=TIM2_VS_ClockSourceINT
VP_TIM3_VS_ClockSourceINT.Mode=Internal
VP_TIM3_VS_ClockSourceINT.Signal=TIM3_VS_ClockSourceINT
board=custom

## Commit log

2024-08-23 First upload, needs tidying!
    [2024-01-08.memorandum.safety-training_electrical-safety_working-in-EP-experiments.v-2-0-0-draftagc_jd_upd_INEx.xlsx, CosmicPiBom1point8extended.xlsx, analog.ki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]
2024-10-24 Delete 2024-01-08.memorandum.safety-training_electrical-safety_working-in-EP-experiments.v-2-0-0-draftagc_jd_upd_INEx.xlsx
    Oops, shouldn't have been in here.
    [2024-01-08.memorandum.safety-training_electrical-safety_working-in-EP-experiments.v-2-0-0-draftagc_jd_upd_INEx.xlsx]
2024-11-22 Beta version upload - alpha mistakes fixed. Added GPS serial to STM32
    [analog.kicad_sch, cosmicpi2beta.csv, cosmicpi2beta.kicad_pcb, cosmicpi2beta.kicad_sch]
2024-11-22 BOM file, as we used for V2.0a with updates and corrections.
    [BOM_as_manf.xlsx]

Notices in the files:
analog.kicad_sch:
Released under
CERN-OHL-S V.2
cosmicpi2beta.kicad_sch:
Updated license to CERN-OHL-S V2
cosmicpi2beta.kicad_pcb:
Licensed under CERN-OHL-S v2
